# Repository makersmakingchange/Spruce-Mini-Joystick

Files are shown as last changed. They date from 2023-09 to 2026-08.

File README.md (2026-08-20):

 # Spruce Mini Joystick

<!---  SUMMARY A brief summary of the project. What it does, who it is for, how much it costs.  --->
The Spruce Mini Joystick is a mini sized proportional joystick that can be used for adaptive gaming or computer access with a suitable adaptor. Based on a generic PS2-style game controller thumbstick, it has range of motion of ±30° and requires approximately 75 grams-force to fully deflect. This joystick has a two output cables, one with a 3.5 mm TRRS audio plug (i.e., headphone jack) for the joystick, and one with a 3.5 mm mono audio plug for the push switch. 

The Spruce Mini Joystick can be used directly as a left or right thumbstick for the [Microsoft Xbox Adaptive Controller (XAC)](https://www.xbox.com/en-CA/accessories/controllers/xbox-adaptive-controller) using the X1 or X2 analog input ports, or directly with the [PlayStation Access Controller](https://www.playstation.com/en-ca/accessories/access-controller/). It can also be used with the [Forest Joystick Mouse Hub](https://github.com/makersmakingchange/Forest-Joystick-Mouse-Hub) as a USB Gamepad or USB Mouse.

The Spruce Mini Joystick is open assistive technology (OpenAT). Under the terms of the open source licenses, the device may be built, used, and improved upon by anyone.

The current version of the Spruce Mini Joystick (v1.0) has been built and internally tested. It is based on a similar design that has been built and user tested.  

<!---  DEVICE PHOTO  --->
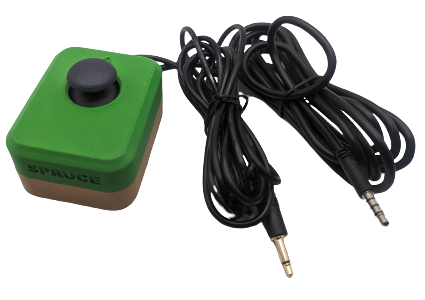
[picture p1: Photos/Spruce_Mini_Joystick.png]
The Spruce Mini Joystick in a brown and green enclosure.
 

**Note:** If experiencing drift when using with the Xbox Adaptive Controller (XAC), unplug and power off the XAC, then power on again and move the joystick in circles.

## Makers Making Change Device Library
  - [Makers Making Change Device Page](https://www.makersmakingchange.com/s/product/spruce-mini-joystick/01tJR000000EHqbYAG)

<!--- 
Other available joysticks can be found through the [Joystick Selection Guide](https://makersmakingchange.com/resource/analog-joystick-selection-guide/)
   --->
   
## OpenAT Joysticks
This design is part of the [OpenAT Joystick project](https://github.com/makersmakingchange/OpenAT-Joysticks), a collection of open source designs for digital access and adapted gaming.  

## How to Obtain a Spruce Mini Joystick
There are several options for obtaining the device.

### 1. Do it Yourself (DIY) or Do it Together (DIT)

This is an open-source assistive technology, so anyone is free to build it. All of the files and instructions required to build the Spruce Mini Joystick are contained within this repository.

### 2. Request a build of this device

If you would like to obtain a Spruce Mini Joystick, you may submit a build request through the [MMC Library Page](https://www.makersmakingchange.com/s/product/spruce-mini-joystick/01tJR000000EHqbYAG). The requestor is responsible for the cost of materials and any shipping.

A limited number of these devices may be available at no-cost to people with disabilities that reside within Canada as part of the [Accesible Technology Program Grant](https://ised-isde.canada.ca/site/accessible-technology-program/en). If you think this applies to you, please send an email to info@makersmakingchange.com.

### 3. How to build this device for someone else
If you have the skills and equipment to build this device, and would like to donate your time to create the joystick for someone who needs it, visit the [MMC Maker Wanted](https://makersmakingchange.com/maker-wanted/) section.

## Getting Started

### 1. Read the Makers Checklist

The Makers Checklist in the [Maker Guide](/Documentation/Spruce_Joystick_Maker_Guide.pdf) contains a list of tasks to complete to build the device.

### 2. Order the Off-The-Shelf Components

The [Spruce Joystick Bill of Materials](/Documentation/Spruce_Joystick_BOM.csv) lists all of the parts and components required to build the Spruce Mini Joystick.

### 3. Print the 3D Printable components

Print the components needed for the Spruce Mini Joystick. Make sure to ask the user if they would like any of the optional prints such as toppers or mount adapters. Refer to the [OpenAT Joystick Setup Guide](https://github.com/makersmakingchange/OpenAT-Joysticks/Resources/OpenAT_Joystick_Setup_Guide.pdf) for detailed mounting options. 

The 3D print files for the mounting adapters are located on the [OpenAT Joystick Repository](https://github.com/makersmakingchange/OpenAT-Joysticks/tree/main/Mounting%20Adapters)

All of the files and individual print files can be in the [/Build_Files/3D_Printing_Files](/Build_Files/3D_Printing_Files/) folder.

### 4. Assemble the Spruce Mini Joystick

Reference the [Maker Guide](/Documentation/Spruce_Joystick_Maker_Guide.pdf) for the tools and steps required to build each portion.

## Files
### Documentation
| Document             | Version | Link |
|----------------------|---------|------|
| Design Rationale     | 1.0     | [Spruce_Mini_Joystick_Design_Rationale](/Documentation/Spruce_Joystick_Design_Rationale.pdf)     |
| Bill of Materials    | 1.0     | [Spruce_Mini_Joystick_Bill_of_Materials](/Documentation/Spruce_Joystick_BOM.csv)     |
| Maker Guide          | 1.0     | [Spruce_Mini_Joystick_Maker_Guide](/Documentation/Spruce_Joystick_Maker_Guide.pdf)     |
| User Guide           | 1.0.1     | [Spruce_Mini_Joystick_User_Guide](/Documentation/Spruce_Joystick_User_Guide.pdf)    |

### Design Files
<!--- DESIGN FILES If possible, include a copy of original design files to facilitate easy editing and customization. --->
 - [CAD Files](/Design_Files)

### Build Files
<!--- BUILD FILES This section lists links to the various files used to build the device. --->
 - [3D Printing Files](/Build_Files/3D_Print_files)

## License
Copyright (c) 2023 Neil Squire / Makers Making Change.

This repository describes Open Hardware:
 - Everything needed or used to design, make, test, or prepare the Spruce Mini Joystick is licensed under the [CERN 2.0 Weakly Reciprocal license (CERN-OHL-W v2) or later](https://cern.ch/cern-ohl ) .
 - Accompanying material such as instruction manuals, videos, and other copyrightable works that are useful but not necessary to design, make, test, or prepare the Spruce Mini Joystick are published under a [Creative Commons Attribution-ShareAlike 4.0 license (CC BY-SA 4.0)](https://creativecommons.org/licenses/by-sa/4.0/) .

You may redistribute and modify this documentation and make products using it under the terms of the [CERN-OHL-W v2](https://cern.ch/cern-ohl).
This documentation is distributed WITHOUT ANY EXPRESS OR IMPLIED WARRANTY, INCLUDING OF MERCHANTABILITY, SATISFACTORY QUALITY AND FITNESS FOR A PARTICULAR PURPOSE.
Please see the CERN-OHL-W v2 for applicable conditions.

Source Location: https://github.com/makersmakingchange/Spruce-Mini-Joystick

## Attribution
<!--- ATTRIBUTION Include any information related to the development of the design. This may include who identified the initial challenge, who contributed to the design --->
Hardware and enclosure design: Josie Versloot, Neil Squire Society

Enclosure design based on [snap assembly thumbstick shell](https://www.printables.com/model/508909-snap-assembly-thumbstick-shell/files) by [AbleGamers Charity](https://ablegamers.org/).

A range of toppers are availablef or this joystick and utilize the mofels found in the [set of toppers created by AbleGamers Charity](https://www.printables.com/model/501869-analog-thumbstick-topper-collection).

The documentation template was created by Makers Making Change / Neil Squire and is used under a CC BY-SA 4.0 license. It is available at the following link: https://github.com/makersmakingchange/OpenAT-Template

---

<!-- ABOUT MMC START -->
## About Makers Making Change
[Makers Making Change Logo](https://www.makersmakingchange.com/)

Makers Making Change is a program of [Neil Squire](https://www.neilsquire.ca/), a Canadian non-profit that uses technology, knowledge, and passion to empower people with disabilities.

Makers Making Change leverages the capacity of community based Makers, Disability Professionals and Volunteers to develop and deliver affordable Open Source Assistive Technologies.

 - Website: [www.MakersMakingChange.com](https://www.makersmakingchange.com/)
 - GitHub: [makersmakingchange](https://github.com/makersmakingchange)
 - Bluesky: [@makersmakingchange.bsky.social](https://bsky.app/profile/makersmakingchange.bsky.social)
 - Instagram: [@makersmakingchange](https://www.instagram.com/makersmakingchange)
 - Facebook: [makersmakechange](https://www.facebook.com/makersmakechange)
 - LinkedIn: [Neil Squire Society](https://www.linkedin.com/company/neil-squire-society/)
 - Thingiverse: [makersmakingchange](https://www.thingiverse.com/makersmakingchange/about)
 - Printables: [MakersMakingChange](https://www.printables.com/@MakersMakingChange)

### Contact Us
For technical questions, to get involved, or to share your experience we encourage you to [visit our website](https://www.makersmakingchange.com/) or [contact us](https://www.makersmakingchange.com/s/contact).
<!-- ABOUT MMC END -->

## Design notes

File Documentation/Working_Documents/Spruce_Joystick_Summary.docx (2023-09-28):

This document is intended to be a summary of a device to make it easier to add to the website.

# Product Information

## Product Name

Spruce Mini Joystick

## Device Category

Adapted Toys

Aids for Daily Living (ADL)

Assistive Switches

Communication Aids (AAC)

Computer Access

Environmental Controls

Gaming

Keyguard

Kits

LipSyncs

Mounting

Recreation and Leisure

Seating and Positioning

Switch Interfaces

Writing Aids

## User Value Statement

If you're looking for a standard joystick with a small range of motion and push button feature, we'd like to point you to the Spruce Mini Joystick.

## Designer

Josie Versloot

# Device Info

## Overview

The Spruce Mini Joystick is a small joystick compatible with the Forest Joystick Mouse Hub (https://github.com/makersmakingchange/Forest-Joystick-Mouse-Hub), Xbox Adaptive Controller, or other analog input joystick devices. It currently has a range of toppers available created by AbleGamers Charity (https://www.printables.com/model/501869-analog-thumbstick-topper-collection).

## Disability Type

Select one or more disability types:

Agility / Dexterity

Arthritis

Cognitive

Hearing

Mobility

Mobility

Other

Pain

SCI

Vision

## Disability Type Description

## This device is designed for users with a small range of motion that need an external joystick for adaptive gaming or computer access.

## How To Use

For full instructions please refer to the User Guide.

Usage

Using the Joystick

1. Plug the 3.5 mm TRRS cable from the joystick into the host device (such as the Xbox Adaptive Controller). If using the Xbox Adaptive Controller, plug it into X1 to use at the left joystick, or plug into X2 to use as the right joystick.

2. Ensure the arrow on the joystick is pointing in the “up/forward” direction, away from the user.

3. Mount the device if needed (see below).

4. Move joystick as you would with a standard controller. Estimated Cost

Compatibility

This device is compatible with the Xbox Adaptive Controller, Forest Joystick Mouse Hub (https://github.com/makersmakingchange/Forest-Joystick-Mouse-Hub), Enabled Controller Mini (https://github.com/makersmakingchange/Enabled-Controller-Mini/tree/main), and any other device that accepts a TRRS analog joystick input.

## Estimated Cost

The estimated material cost of the device:

$0 - $10

$11 - $25

$26 - $50

$51 - $100

$101 - $250

$250+

## Attribution

Hardware and enclosure design: Josie Versloot, Neil Squire Society

Enclosure design remixed from AbleGamers Charity (https://www.printables.com/model/508909-snap-assembly-thumbstick-shell/files), originally released under a Creative Commons (4.0 International License) Attribution-NonCommercial

(http://creativecommons.org/licenses/by-nc/4.0/)

The documentation template was created by Makers Making Change / Neil Squire and is used under a CC BY-SA 4.0 license. It is available at the following link: https://github.com/makersmakingchange/OpenAT-Template

# Maker Info

## Project Skills

3D Printing

Custom PCB

Electronics

Laser Cutting

Mechanics

Other

Software

Soldering

Woodworking

## Skills Description

This is an intermediate build requiring electronics, mechanics, and 3D printing.

## Tools Needed

3D Printer

Common Hand Tools

Common Power Tools

Laser Cutter

Soldering Iron

Specialized Tooling

## Print time (hrs)

<Estimated total print time in numerical hours>

## Assembly time (hrs)

<Estimated assembly time in numerical hours>

## Build Instructions

For full instructions please refer to the Maker Guide.

Print Settings:

- 0.2mm Layer Height
- 20% infill

## Download Link

https://github.com/makersmakingchange/Spruce-Mini-Joystick/archive/refs/heads/main.zip

## Project Link

https://github.com/makersmakingchange/Spruce-Mini-Joystick

# License

## License

Hardware: CERN OHL 2.0 w

Documentation: Attribution-ShareAlike 4.0 International

© 2023 by Neil Squire Society. This work is licensed under the CC BY SA 4.0 License: http://creativecommons.org/licenses/by-sa/4.0 Files available at https://github.com/makersmakingchange/Spruce-Mini-Joystick Page 1 of 2

V1.0 | September 2023 Spruce Mini Joystick Summary

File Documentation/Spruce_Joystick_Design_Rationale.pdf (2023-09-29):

V1.0 | SEPTEMBER 2023

## Spruce Mini Joystick

## DESIGN RATIONALE

© 2023 by Neil Squire Society. (https://www.neilsquire.ca/) This work is licensed under the CC BY SA 4.0 License: http://creativecommons.org/licenses/by-sa/4.0 Files available at https://github.com/makersmakingchange/Spruce-Mini-Joystick

### Introduction

There is an identified need for cost-effective analog joysticks that can be used with the Xbox Adaptive Controller (XAC). There are currently not very many commercial joysticks on the market, and the ones that are can be costly. This joystick is intended to be used with the XAC for anyone who may find it easier to game with a joystick.

There is also a need for alternative mouse options that are affordable, and some people may find a joystick easier to use than a standard mouse. This mouse needs to be a standalone device or combination of devices that can be used with PC and can complete the basic mouse functions such as left click.

This joystick specifically is meant for someone with a lower range of motion and lower force compared to some USB joysticks.

### Research

### Commercial Joysticks

Name | Price | Link | Picture
Ultra-Stik | 95 UK | Accessible Gaming Shop -Ultra-Stik -OneSwitch.org.uk (https://www.oneswitch.org.uk/art.php?id=17)

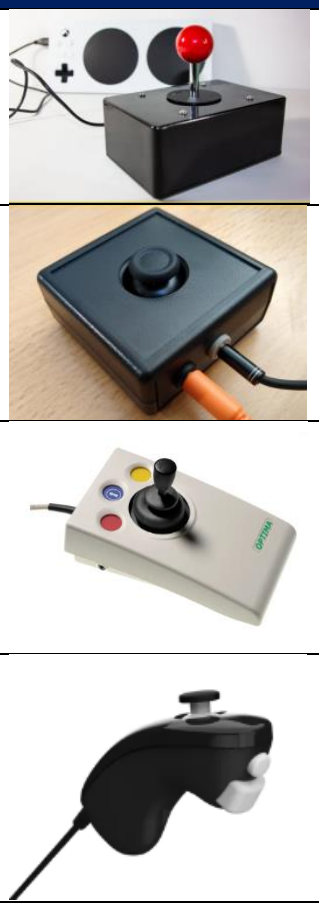
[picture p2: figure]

XAC MINI Stick | 105 UK | XAC Mini Joystick -OneSwitch.org.uk (https://www.oneswitch.org.uk/art.php?id=270)
Optima Joystick | 219.60 UK | Optima Joystick - Video Gaming Assistive Joystick (pretorianuk.com) (https://www.pretorianuk.com/optima-joystick)
PDP One-Handed Joystick for Xbox Adaptive Controller | Discontinued | PDP One-Handed Joystick for Xbox Adaptive Controller (microsoft.com) (https://www.microsoft.com/en-ca/d/pdp-one-handed-joystick-for-the-xbox-adaptive-controller/8qhw8mlwpp1l)

## DESIGN RATIONALE

© 2023 by Neil Squire Society. (https://www.neilsquire.ca/)

XAC Flat Thumbstick | $74.95 | XAC Flat Thumbstick (evilcontrollers.com) (https://www.evilcontrollers.com/xac-flat-thumbstick)

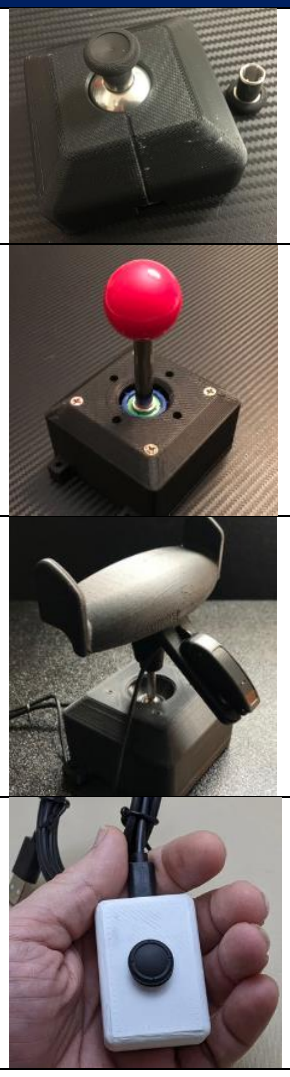
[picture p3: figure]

Name | Price | Link | Picture
MINISTIX-TU | $75 | MINISTIX-TU (USB Version) — Warfighter Engaged (https://warfighterengaged.org/shop/ministix-tu)
DPAD-T | $65 | DPAD-T — Warfighter Engaged (https://warfighterengaged.org/shop/dpad-t)
JOYSTIX-FPS | $75 | JOYSTIX-FPS — Warfighter Engaged (https://warfighterengaged.org/shop/joystix-l-aenef)
JoyCon® Style Joystick For XBOX® Adaptive Controller & PC (JoyToKey) | $60.40 | Joycon® Style Joystick for XBOX® Adaptive Controller & PC | Etsy Canada (https://www.etsy.com/ca/listing/1205880837/joycon-style-joystick-for-xbox-adaptive?click_sum=ba40a784&crt=1)

### Ideation

### Joystick Element

For this design, the same joystick element will be used as the current Analog Thumbstick on the website, which is a standard PS2 thumbstick unit.

There is also an Adafruit version of a similar joystick, this will be investigated as well and the price and availability will be compared.

### Switch Input

There are a few different ways that switch input can be accomplished:

## DESIGN RATIONALE

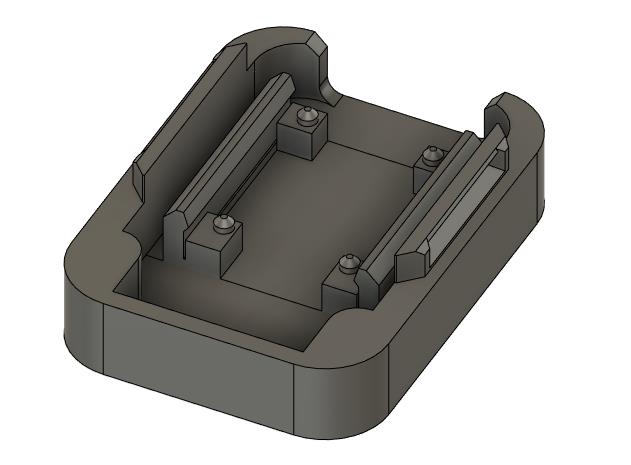
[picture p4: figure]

© 2023 by Neil Squire Society. (https://www.neilsquire.ca/)

- Integrated buttons
- Integrated switch jacks
- Separate “controller box” that the joystick and switches plug into

The first iteration of this design is now the Cedar Mini Joystick which had integrated jacks, where the users could plug in their assistive switch of choice for switch input. While in mouse mode, these switches are left click, right click, and scroll.

After user testing, the decision was made to proceed with the separate “controller box” or “hub” that the joystick and switches plug into.

### Conceptual Design

The enclosure design for this joystick was based on the AbleGamers “snap assembly thumbstick shell” in Printables. (https://www.printables.com/model/508909-snap-assembly-thumbstick-shell)

### Concept 1: Joystick snap in assembly

For this, the joystick would snap into the enclosure like it does in the original AbleGamers design.

## DESIGN RATIONALE

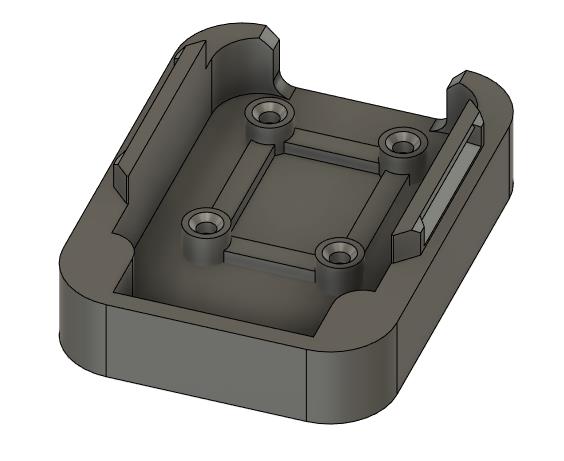
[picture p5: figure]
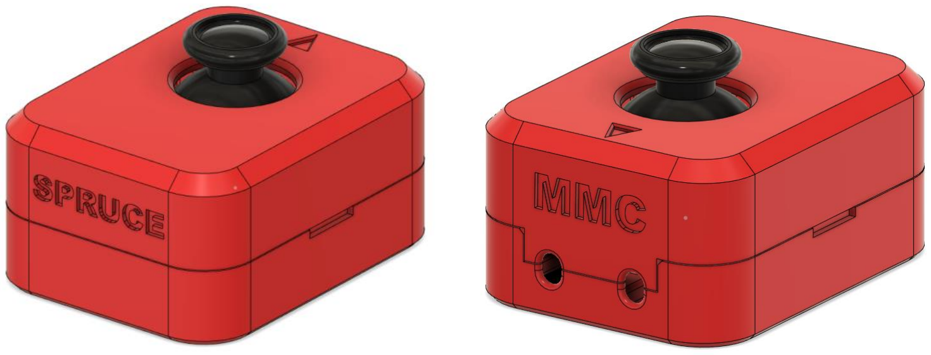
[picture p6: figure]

© 2023 by Neil Squire Society. (https://www.neilsquire.ca/)

### Concept 2: Joystick screw in assembly

### Detailed Design

### Overview

On the outside of the enclosure, there are a few key features. On the side facing the user, “Spruce” is engraved, and on the side facing away from the user “MMC” is engraved. There is also an arrow on the top of the enclosure showing the up direction.

There are two cables that exit the back side of the enclosure (away from the user), both are 3.5 mm audio cables. One of the cables has 4 conductors (TRRS cable) for the joystick output, and one has 2 conductors (mono cable) for the switch output for the press down switch built into the joystick. It was

## DESIGN RATIONALE

© 2023 by Neil Squire Society. (https://www.neilsquire.ca/) decided that these cables would exit away from the user for better cable management and to be the most out of the way while the joystick is in use.

Joystick Unit
For this joystick, there are two main joystick/thumbstick units that can be used. Some are commercially available for hobbyists from a few different sources such as Amazon, and then the other unit is the “Adafruit 2-axis Thumb Joystick with Select Button + Breakout Board” which available from some electronics suppliers such as DigiKey and Mouser.

Comparing these two joystick units, the ones from Amazon are significantly less expensive, at $20.89 for a pack of 10, whereas the Adafruit unit is $9.13 on DigiKey for one unit. For a single build the Adafruit unit would be less expensive, but for 2 or more units it would make sense to use the units from Amazon.

Another consideration here is availability. The Adafruit unit goes in and out of stock, but when it comes back in stock it is the same unit. There seem to be more Amazon units in stock, but they could go out of stock at any time. If they go out of stock a comparable unit can often be found, but it might not be exactly the same, which leads to the point of consistency across units.

Lastly, the consistency and quality of the joystick unit should be considered. The Adafruit unit is going to be more consistent and is guaranteed to always be the same dimensions and quality. Whereas if the Amazon unit goes out of stock and another unit has to be sourced it is not guaranteed to be exactly the same, and the hole spacing and overall quality could be different.

For this iteration of the design, two sets of holes were included so either joystick unit could be used.

### Wiring

Wiring diagram
To wire the joystick the Xbox Adaptive Controller analog input convention will be used with a 3.5 mm TRRS audio cable. Since the joystick has a built-in button as well, an additional 3.5 mm mono audio cable will be used as well.

Table 1. XAC Analog Joystick Input Convention

JOYSTICK | TRRS PLUG
X-AXIS | Tip
Y-AXIS | Ring 1
GND | Ring 2
VCC | Sleeve

## DESIGN RATIONALE

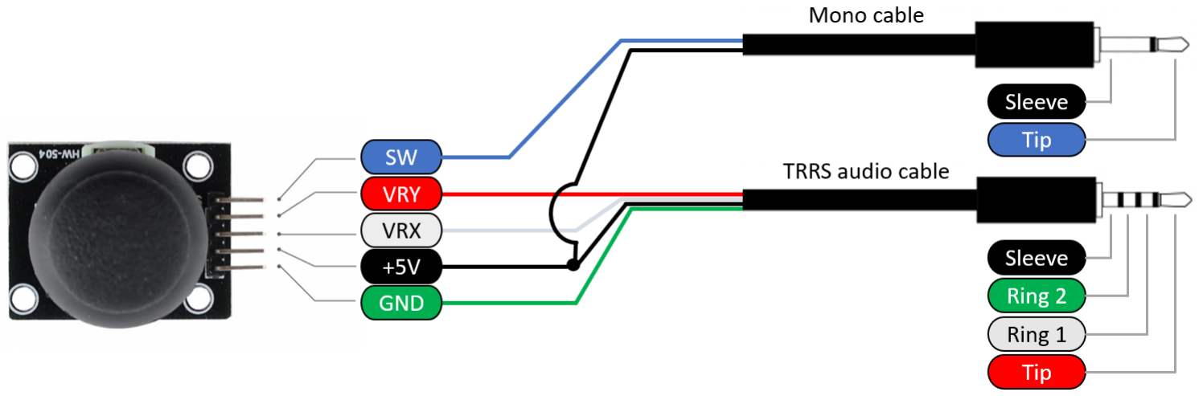
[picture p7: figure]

© 2023 by Neil Squire Society. (https://www.neilsquire.ca/)

Generic PS2 Joystick Wiring

Figure 1. Generic PS2 Wiring Diagram

Table 2. Generic PS2 Wiring Guide

JOYSTICK BOARD LABEL | DIGIKEY TRRS CABLE | TRRS PLUG | MONO CABLE | MONO PLUG
SW | --- | --- | Red | Tip
VRY | Red | Tip | | ---
VRX | White | Ring 1 | | ---
+5V | Black | Sleeve | | ---
GND | Green | Ring 2 | White | Sleeve
Table 1 lists the wiring connections and colors for the DigiKey TRRS and mono cables.

## DESIGN RATIONALE

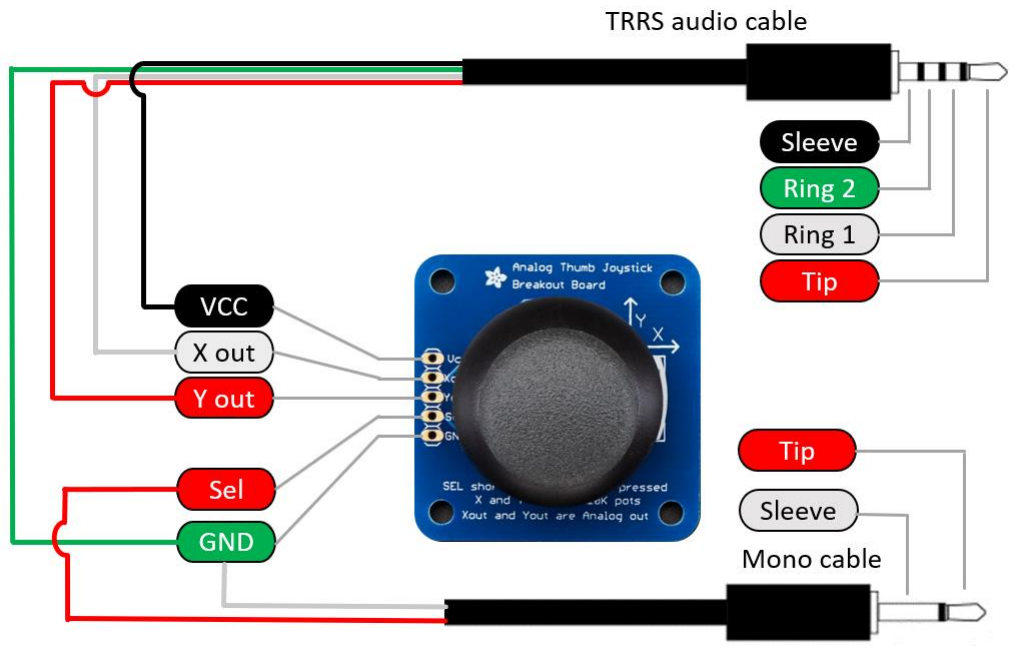
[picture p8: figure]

© 2023 by Neil Squire Society. (https://www.neilsquire.ca/)

Adafruit Joystick Wiring

Adafruit Joystick Wiring diagram

Figure 2. Adafruit Joystick Wiring Diagram

Table 3. Adafruit Joystick Wiring

JOYSTICK BOARD Label | TRRS Plug | DigiKey TRRS Cable | Your TRRS CABLE | Mono PLUG | Mono CABLE | Your Mono Cable
Sel | --- | --- | | Tip | Red
Yout | Tip | Red | | --- | ---
Xout | Ring 1 | White | | --- | ---
Vcc | Sleeve | Black | | --- | ---
GND | Ring 2 | Green | | Sleeve | White

## DESIGN RATIONALE

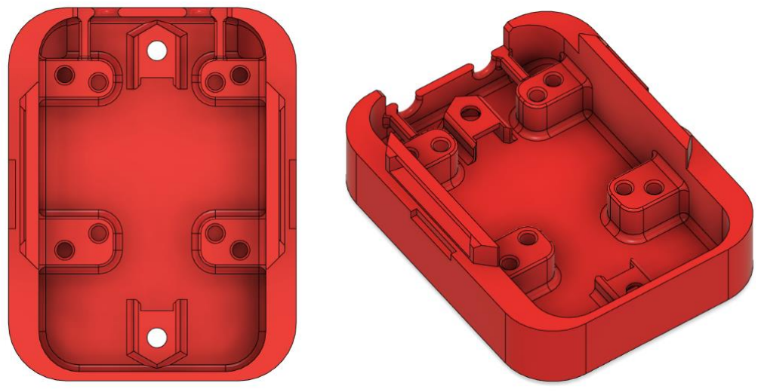
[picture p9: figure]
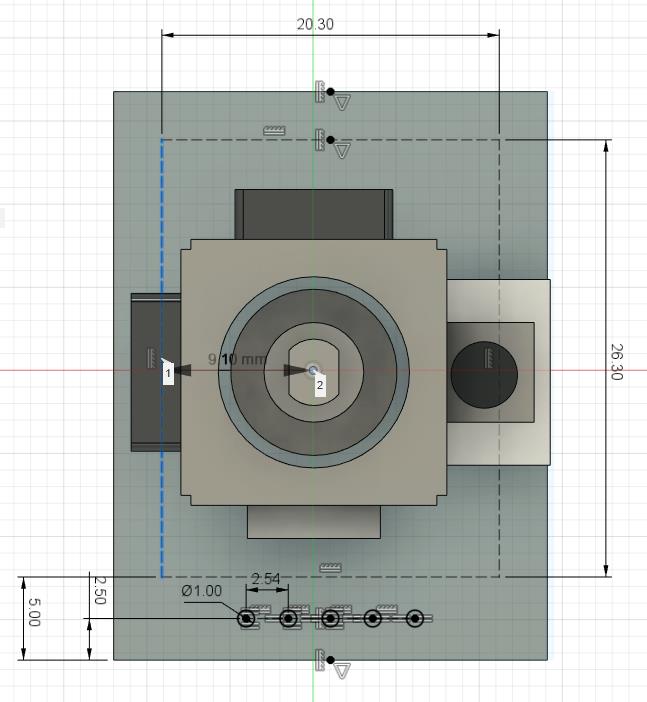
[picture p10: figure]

© 2023 by Neil Squire Society. (https://www.neilsquire.ca/)

### Enclosure Bottom

Joystick Mounting
For the two sets of mounting holes, it was decided to use a #4 sheet metal self tapping screw like other MMC designs such as the Oak Compact Joystick and the MMC60 switch. The thread diameter of this screw is 2.8 mm, and the best practice for the hole size for self tapping screws (https://www.hydraresearch3d.com/design-rules#threads-post-process) is 96% of the hole diameter, so a hole size of 2.68 mm was used.

The spacing of the holes for the Amazon unit is seen below:

The Adafruit joystick unit has the holes in a square with the joystick centered between the screw holes. The spacing of these screw holes is 30.48 mm as seen below:

## DESIGN RATIONALE

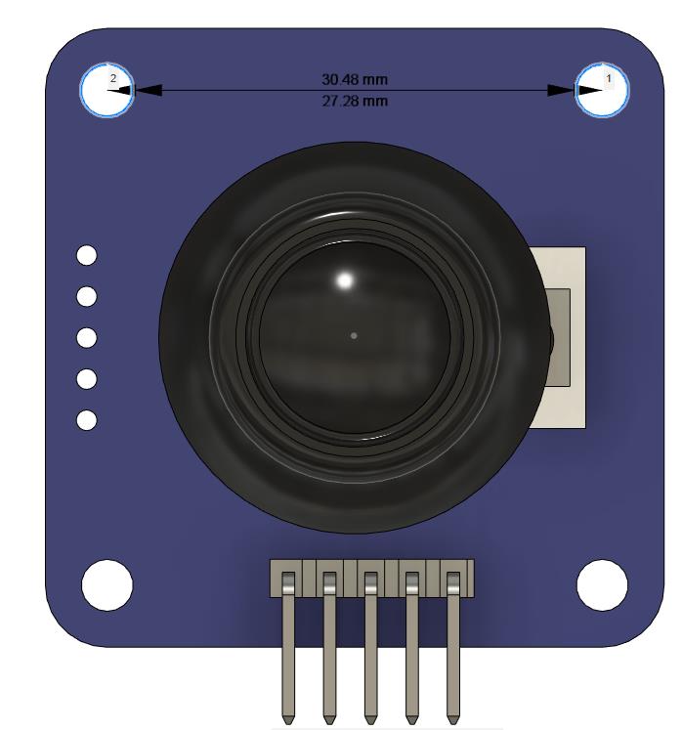
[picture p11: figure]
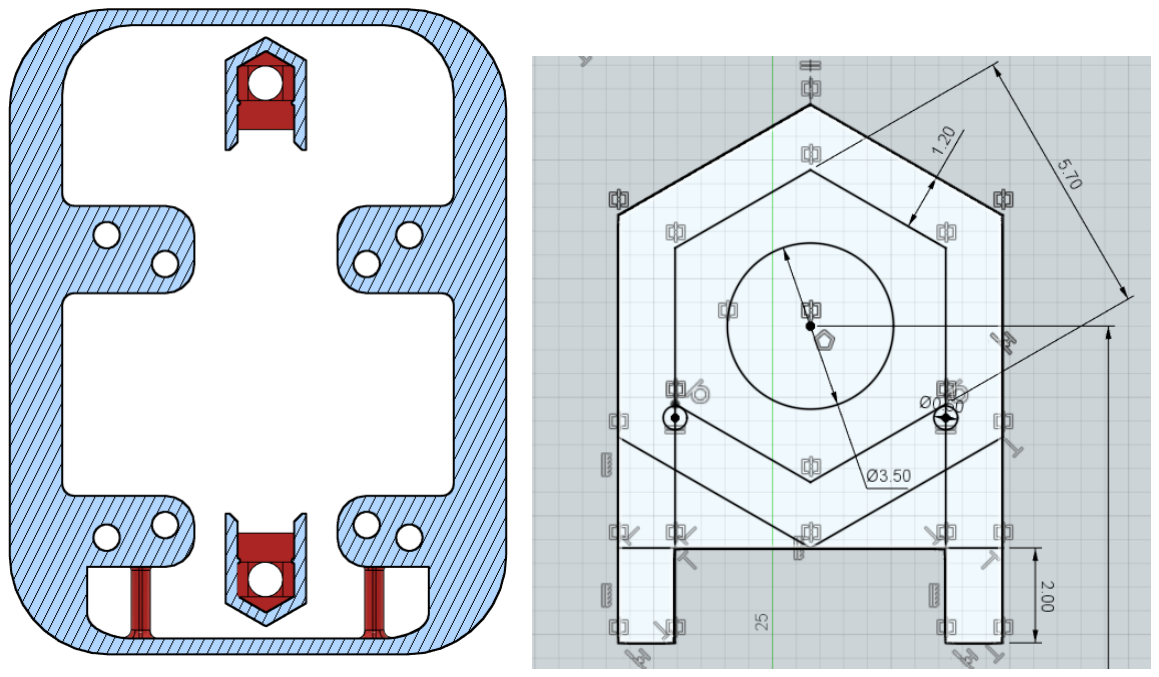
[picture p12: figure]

© 2023 by Neil Squire Society. (https://www.neilsquire.ca/)

Mounting – Captive Nuts
It was decided that this design should incorporate a way to mount the joystick when not used on a tabletop. To do this, two slots for captive nuts were added, which would then screw into a separate mount adapter which will have the mounting hardware in it. Here, two M3 hex nuts are used. The centres of these nuts are 50.0 mm apart. There are also small walls added coming out of these captive nut slots to help with alignment of the nut while inserting. These two slots are seen in the photos above, and then in a closer view below. As seen in the photo, around the hole above the captive nut, which would be printed unsupported, there are small single layer rectangles, this is a best practice when 3D printing unsupported holes. (https://www.hydraresearch3d.com/design-rules#unsupported-holes)

## DESIGN RATIONALE

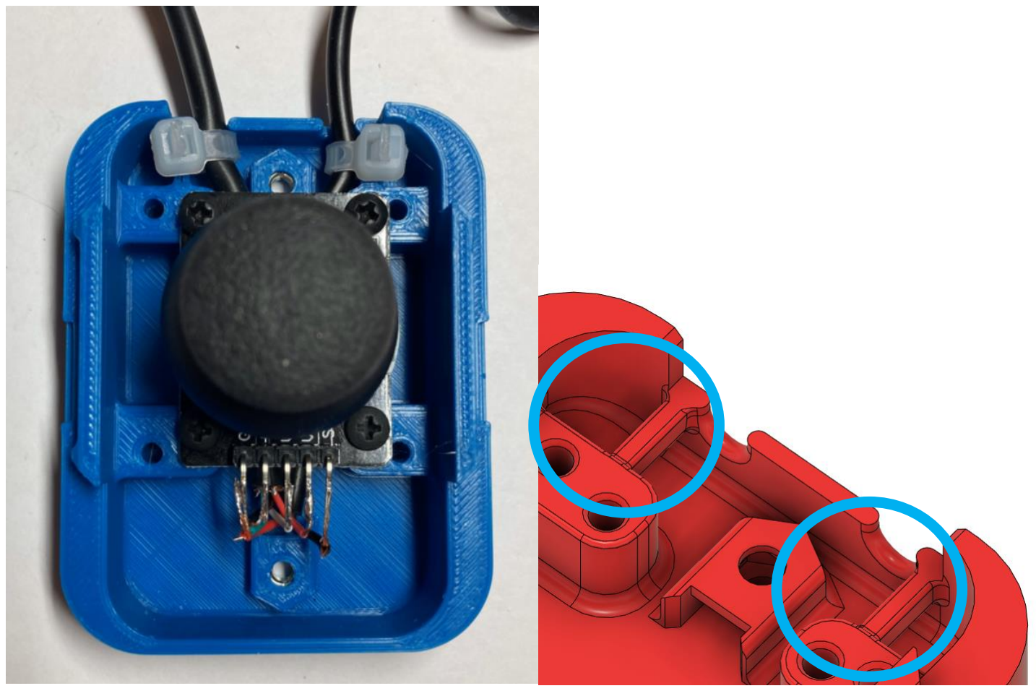
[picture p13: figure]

© 2023 by Neil Squire Society. (https://www.neilsquire.ca/)

Cable Strain Relief

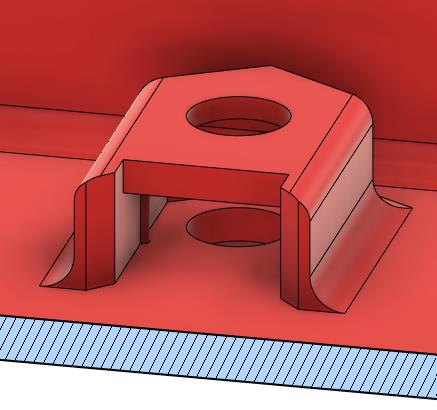
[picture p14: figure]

Strain relief for the two cables exiting the enclosure was added by adding two small beams where a zip tie could be fastened for each of the cables before they exit the enclosure. The zip ties are shown with the cables in the photo below, and the beams are circled in a picture from the CAD.

Enclosure Snap Fit
This design uses a snap fit to connect the top of the enclosure to the bottom of the enclosure.

The piece on the bottom of the enclosure was extruded inwards (cut away from body) 3mm at a taper angle of 45 degrees. The top lip was then chamfered so the top could be inserted easier. The same sketch was used for the top of the enclosure to extrude out 3 mm at a taper angle of 45 degrees, and then the tip was chamfered. The distance between the two surfaces before adding the snap fit was 0.3mm.

## DESIGN RATIONALE

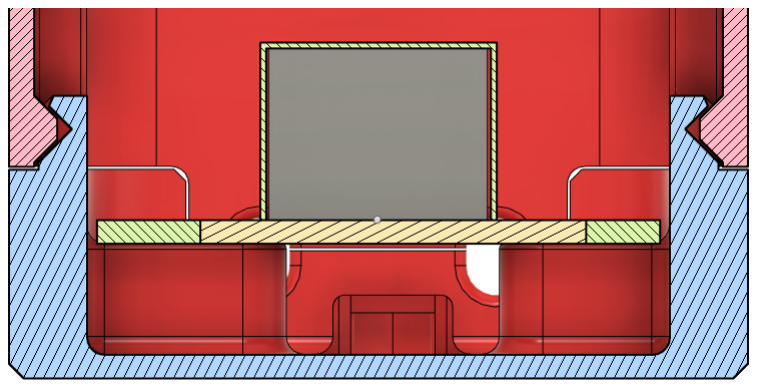
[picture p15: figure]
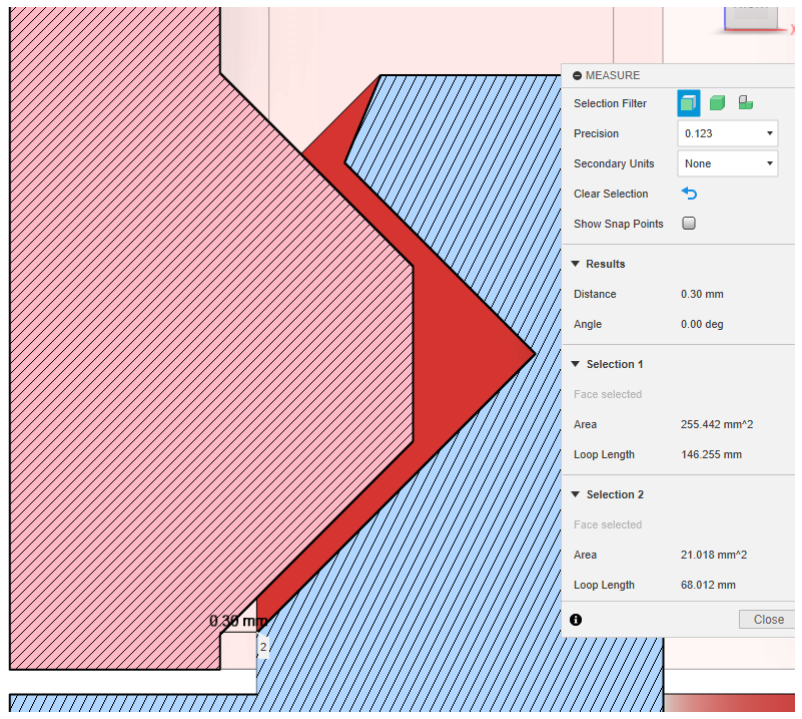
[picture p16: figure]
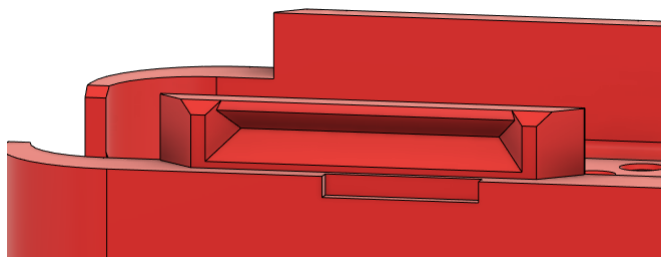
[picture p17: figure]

© 2023 by Neil Squire Society. (https://www.neilsquire.ca/)

Piece on the bottom enclosure:

Piece on the top enclosure:

## DESIGN RATIONALE

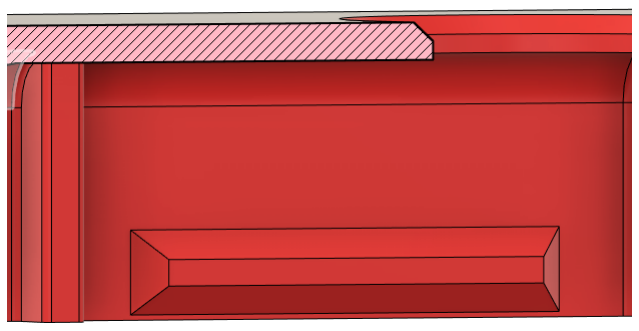
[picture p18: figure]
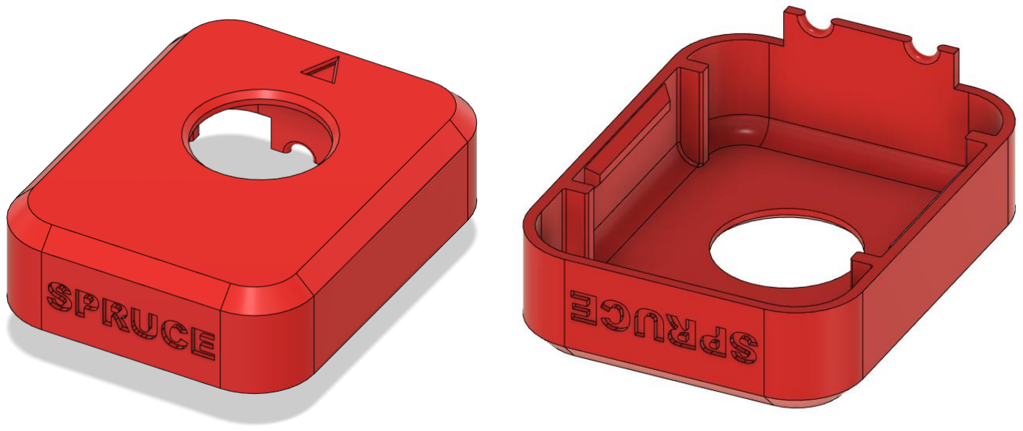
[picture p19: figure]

© 2023 by Neil Squire Society. (https://www.neilsquire.ca/)

### Enclosure Top

During User Testing with the Cedar Mini Joystick (which used the same joystick unit) it was identified that it is important to not have a large gap between the joystick unit and the enclsoure, where the electronisc can be seen and things could fall into the enclosure during use, such as crumbs or other debris. For this reason, the height on this enclosure was increased and the size of the hole around the joystick was decreased, to decrease this gap.

## DESIGN RATIONALE

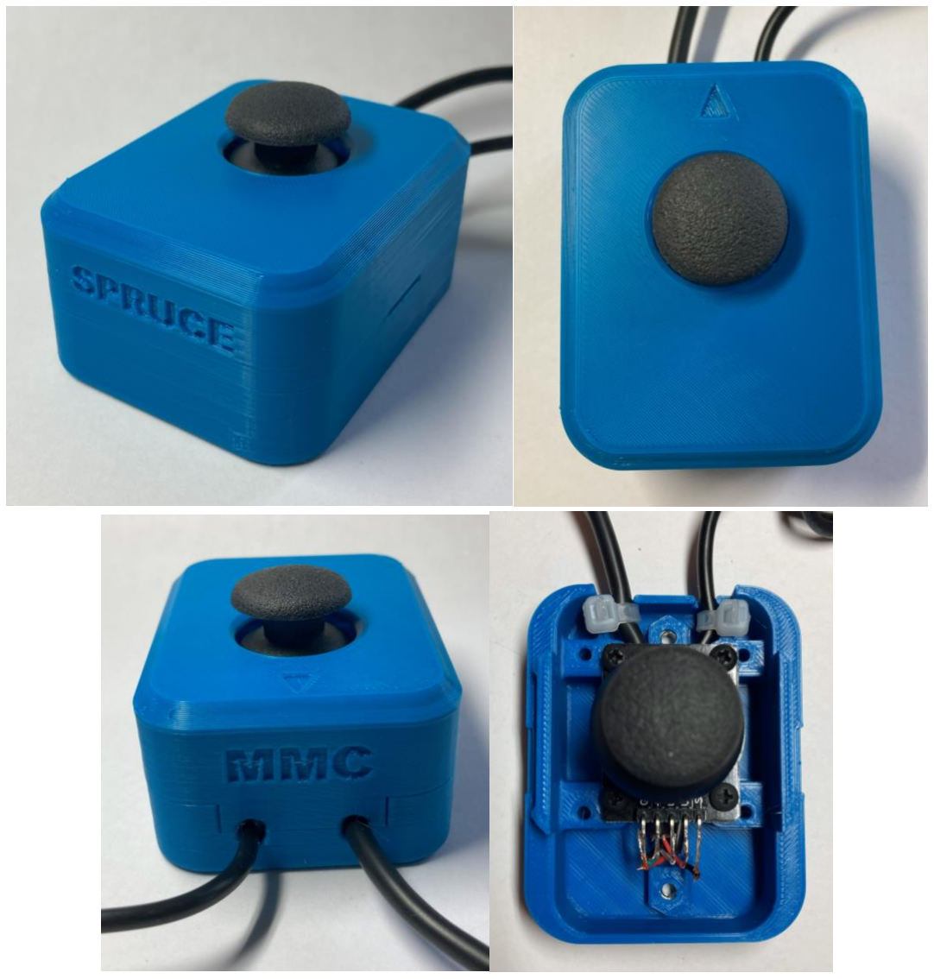
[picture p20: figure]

© 2023 by Neil Squire Society. (https://www.neilsquire.ca/)

### Assembled Prototype

### Opportunities for Improvement

- Could reduce the height of the enclosure, if possible to keep the fit around the joystick topper
- Add a feature to the outside of the enclosure to allow for snap on pieces for wrist supports and other bases

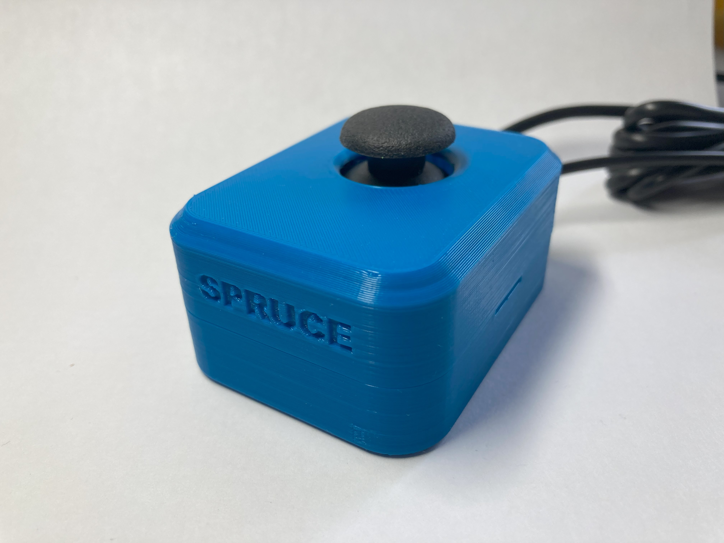
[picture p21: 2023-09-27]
Photos/Spruce_Mini_Joystick_front.jpg

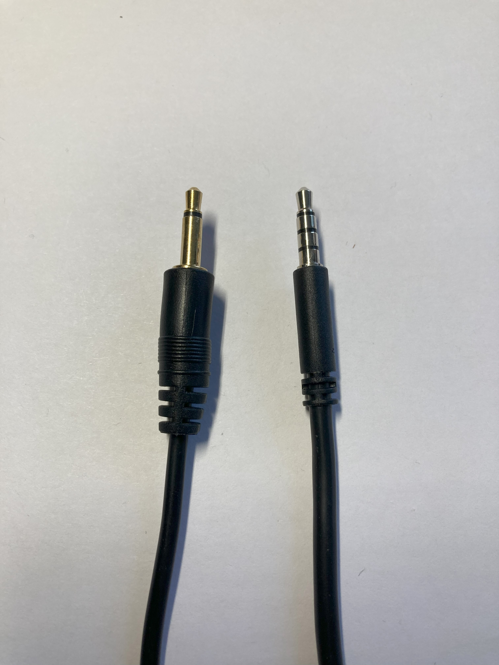
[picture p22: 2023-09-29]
Photos/Mono_and_TRRS_cables.jpg

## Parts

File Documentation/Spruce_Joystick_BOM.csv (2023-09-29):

Spruce Mini Joystick |  |  |  |  |  |  |  | Unit Cost | Total Cost | Total Print time (hr) | Total filament (g)
Version: V1.0 |  | Last Updated: 2023-Sept-25 |  |  |  |  |  | $33.18 | $33.18 | 3.13 | 28
Commercial Parts
 | Part Name | Source | QTY | QTY/PKG | $/PKG | PKG QTY | $/Unit | Extended | Total | Link
 | Joystick unit - Adafruit | DigiKey | 1 | 1 | 9.13 | 1 | $9.13 | $9.13 | $9.13 | https://www.digikey.ca/en/products/detail/adafruit-industries-llc/512/7056915
 | TRRS 3.5 mm Audio Cable | DigiKey | 1 | 1 | $7.29 | 1 | $7.29 | $7.29 | $7.29 | https://www.digikey.ca/en/products/detail/tensility-international-corp/10-00341/2350244
 | Mono 3.5 mm Audio cable | DigiKey | 1 | 1 | $4.62 | 1 | $4.62 | $4.62 | $4.62 | https://www.digikey.ca/en/products/detail/tensility-international-corp/10-00344/2350247
 | 4" cable tie | DigiKey | 2 | 1 | $0.25 | 2 | $0.25 | $0.50 | $0.50 | https://www.digikey.ca/en/products/detail/te-connectivity/2-604771-9/2259327
 | #4 Metal Screw, 3/8″ Length (if building more than two, link below) | DigiKey | 4 | 1 | $0.60 | 4 | $0.60 | $2.40 | $2.40 | https://www.digikey.ca/en/products/detail/serpac/6005/307599
 | M3 hex nut | DigiKey | 2 | 1 | $0.27 | 2 | $0.27 | $0.54 | $0.54 | https://www.digikey.ca/en/products/detail/keystone-electronics/4708/4499301
 | Digikey shipping (if spending less than $100) | DigiKey | 1 | 1 | $8.00 | 1 | $8.00 | $8.00 | $8.00
3D Printed Parts ESTIMATED PRICING USING 1KG ROLL COST: |  | $25.00
 | Part | Material | QTY | Mass (g) / Unit | Time / Unit |  | Print Time (Min) | Estimated Price |  | Link
 | Spruce Enclosure Bottom | PLA | 1 | 16 | 106 |  | 106 | $0.40
 | Spruce Enclosure Top | PLA | 1 | 12.0 | 82 |  | 82 | $0.30
Alternatives
ID | Part and description | Source | QTY | QTY/PKG | $/PKG | PKG QTY | $/Unit | Extended | Total | Link
 | #4 Metal Screw, 3/8″ Length, 100 pack | Amazon | 8 | 100 | $9.30 | 1 | $0.09 | $0.74 | $9.30 | https://a.co/d/523bJeL
 | Cable tie | DigiKey | 1 | 1 | $0.15 | 1 | $0.15 | $0.15 | $0.15 | https://www.digikey.ca/en/products/detail/heyco-products-corporation/13123B/15791902
 | Cable tie | Your local dollarstore
 | Joystick (PS2) | Amazon | 1 | 10 | $20.89 | 1 | $2.09 | $2.09 | $20.89 | https://www.amazon.ca/dp/B089VXPHDH?_encoding=UTF8&psc=1&ref_=cm_sw_r_cp_ud_dp_GGTEDME4PM2P27SG86P7
 | Joystick unit - Adafruit | Mouser | 1 | 1 | 8.63 | 1 | $8.63 | $8.63 |  | https://www.mouser.ca/ProductDetail/Adafruit/512?qs=GURawfaeGuBuwf9HaRK7%252BA%3D%3D
 | (Optional for mount) M3x12mm screw x2 | Mechanical | 0 | 1 | $1.11 | 0 | $1.11 | $- | $- | https://www.digikey.ca/en/products/detail/apm-hexseal/RM3X12MM-2701/2063201
 | (Optional for mount) Tee nut (source from local hardware store) | Mechanical | 0 | 1 | $0.48 | 0 | $0.48 | $- | $- | https://www.homedepot.ca/product/paulin-1-4-inch-20-tee-nuts-4-prong-5-16-inch-barrel-length/1000129429

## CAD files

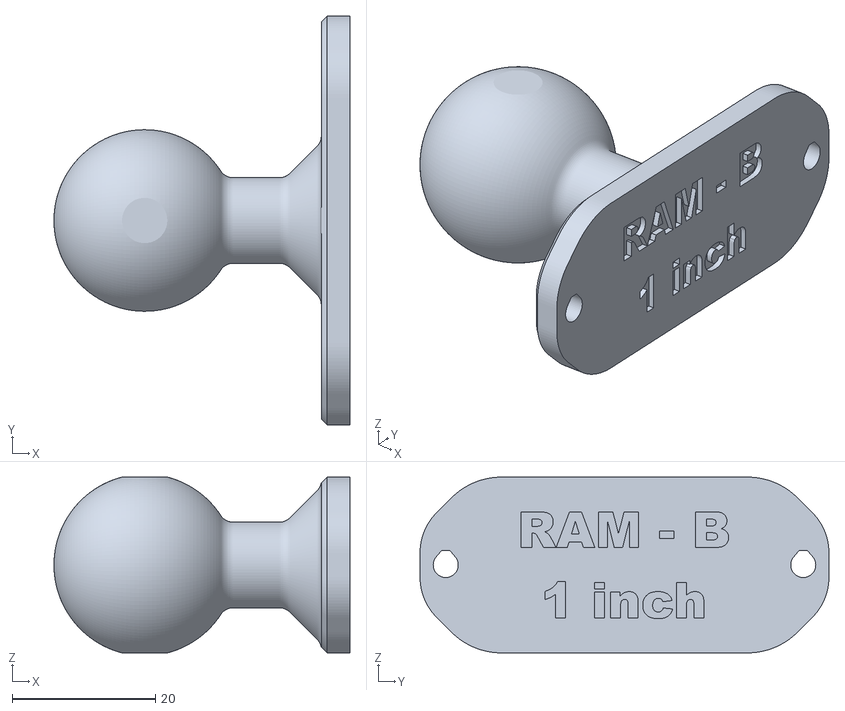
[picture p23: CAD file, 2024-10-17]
Build_Files/3D_Printing_Files/Joystick_RAM_B_Mount_Adapter.stl
41.4 x 57.2 x 24.6

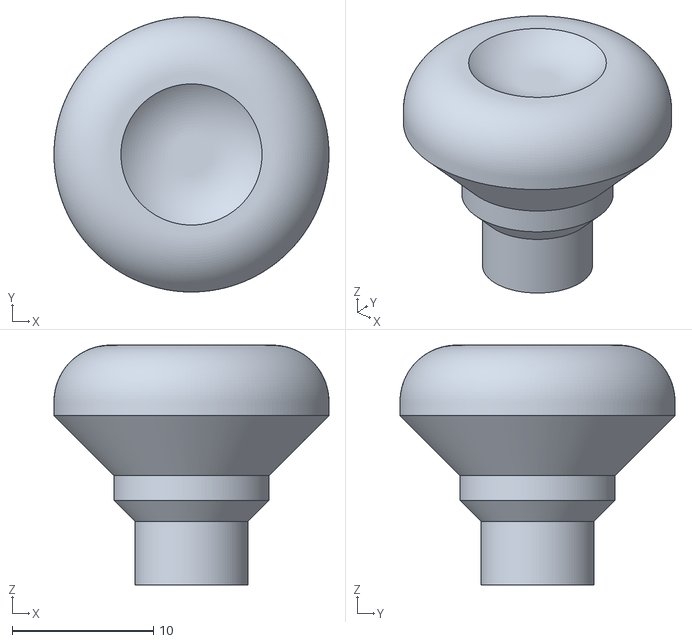
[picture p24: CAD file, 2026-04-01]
Build_Files/3D_Printing_Files/Toppers/Additional_Toppers/standard.stl
19.5 x 19.5 x 17.0

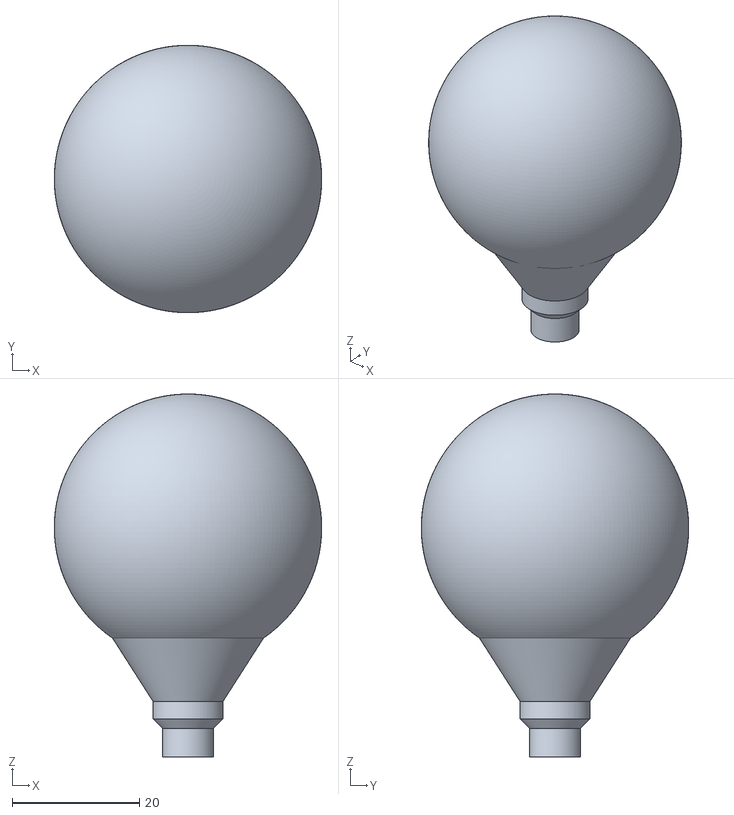
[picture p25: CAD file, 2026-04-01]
Build_Files/3D_Printing_Files/Toppers/Ball_Topper.stl
42.0 x 42.0 x 57.0

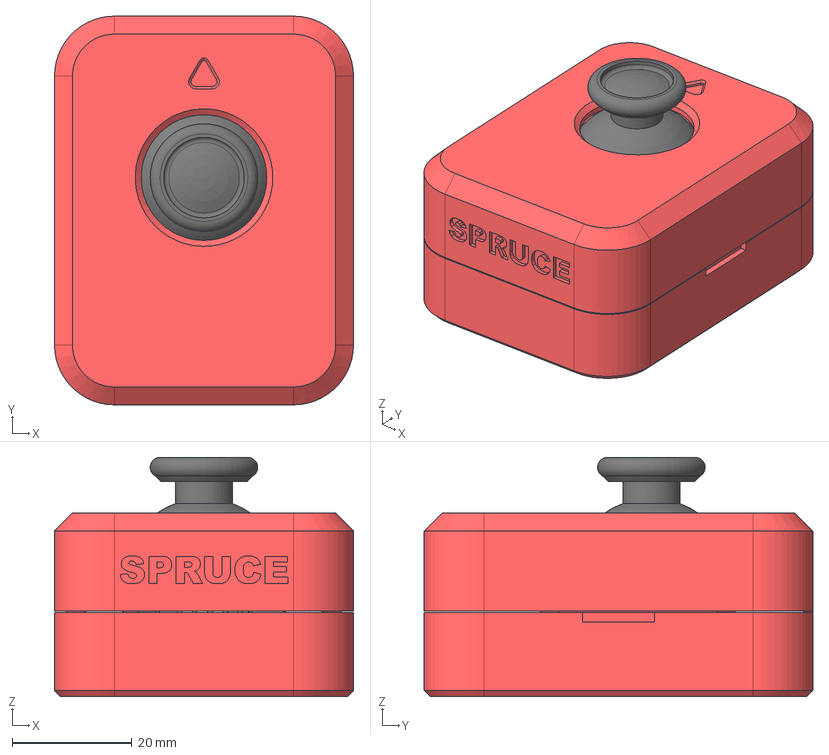
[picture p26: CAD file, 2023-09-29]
Design_Files/CAD_Design_Files/Spruce_Mini_Joystick.step
50.0 x 65.0 x 40.0 mm
shell bottom
shell top
Adafruit 512 Analog 2-axis Joystick v1
Cover
Male Header Right Angle 5 Pin

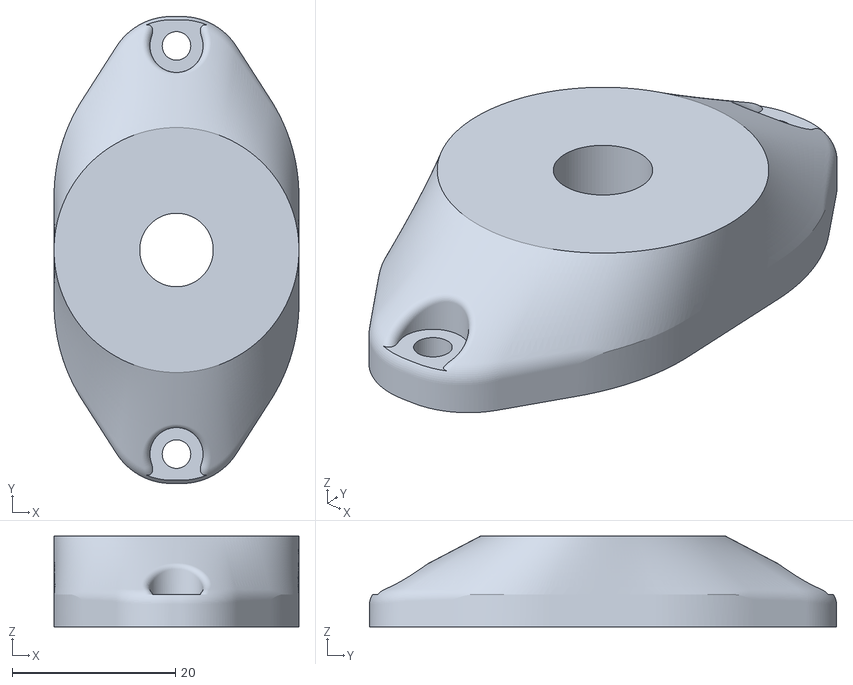
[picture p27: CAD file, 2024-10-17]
Build_Files/3D_Printing_Files/Joystick_Camera_Mount_Adapter.stl
30.0 x 57.2 x 11.1

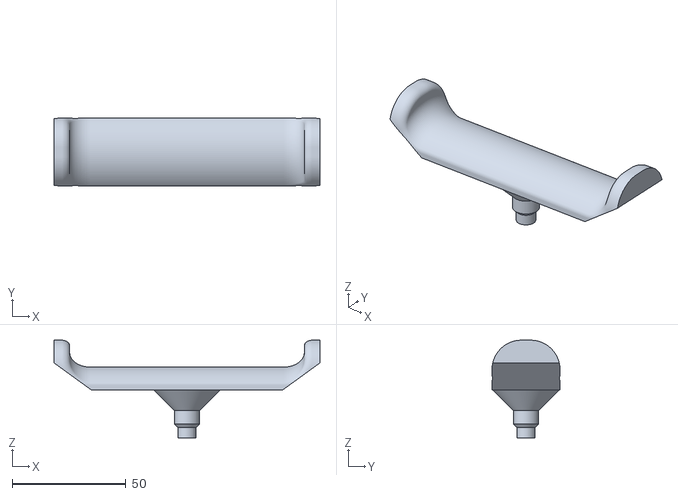
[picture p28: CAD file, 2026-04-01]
Build_Files/3D_Printing_Files/Toppers/Additional_Toppers/thumbstick-super-wide.stl
117.1 x 30.0 x 43.0

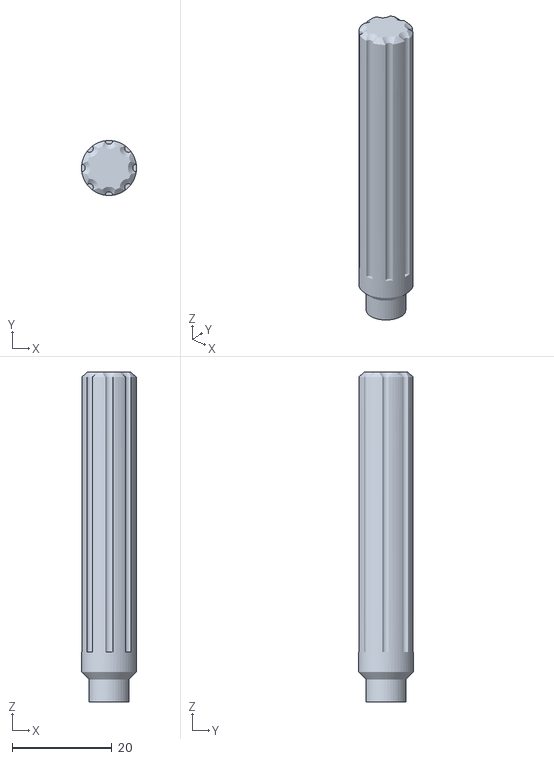
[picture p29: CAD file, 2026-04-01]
Build_Files/3D_Printing_Files/Toppers/Stick_Topper.stl
11.0 x 11.0 x 66.0

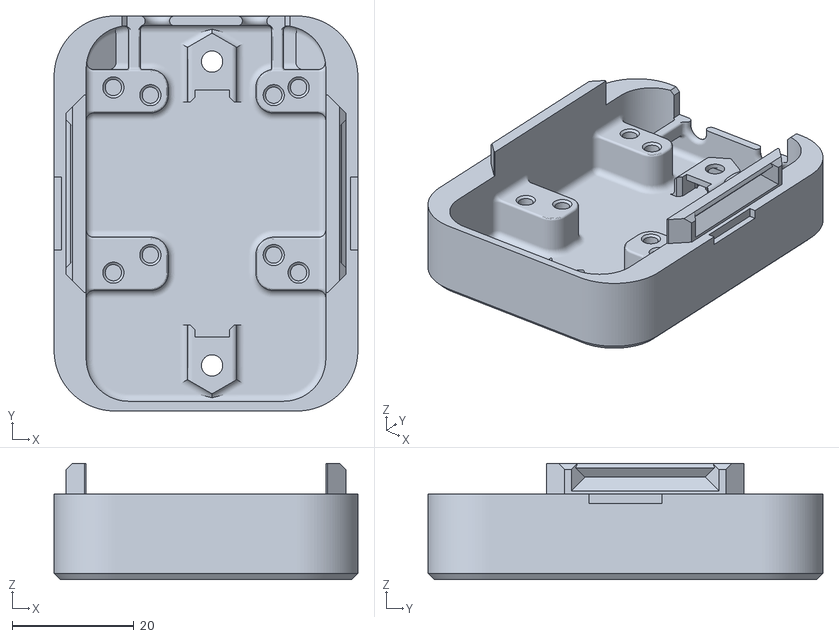
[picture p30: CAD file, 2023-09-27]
Build_Files/3D_Printing_Files/Spruce_enclosure_bottom.stl
50.0 x 65.0 x 19.1

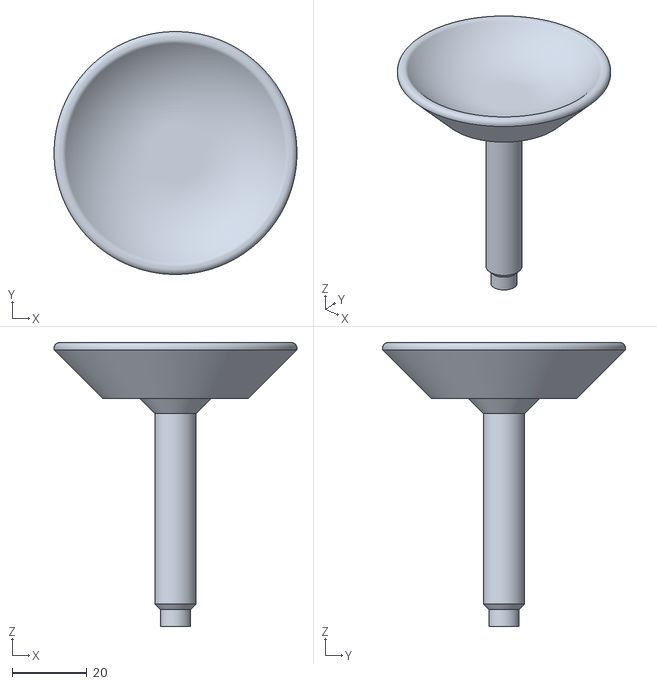
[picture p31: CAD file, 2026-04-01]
Build_Files/3D_Printing_Files/Toppers/Additional_Toppers/chin_cup.stl
65.0 x 65.0 x 76.0

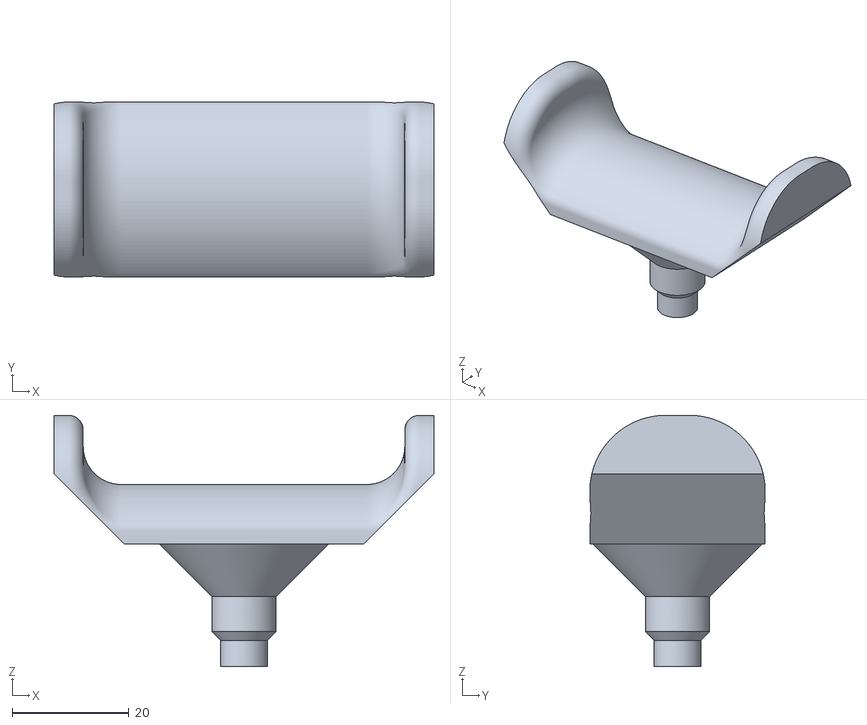
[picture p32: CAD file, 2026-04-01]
Build_Files/3D_Printing_Files/Toppers/Small_Goalpost_Topper.stl
65.0 x 30.0 x 43.0

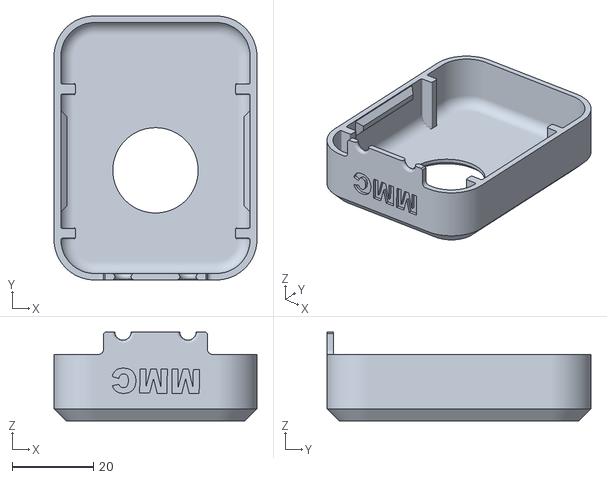
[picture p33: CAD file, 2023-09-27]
Build_Files/3D_Printing_Files/Spruce_enclosure_top.stl
50.0 x 65.0 x 21.9

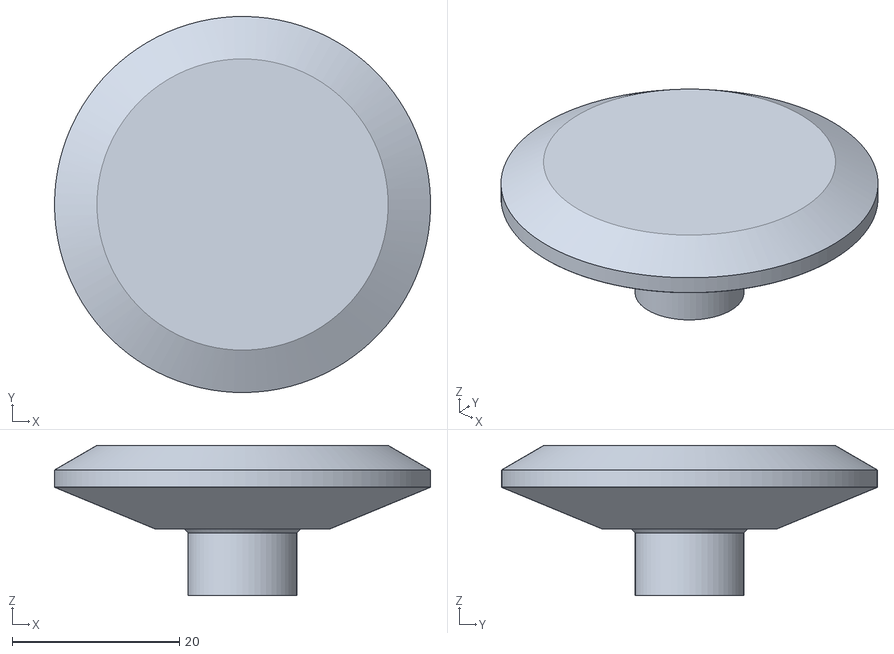
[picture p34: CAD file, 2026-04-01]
Build_Files/3D_Printing_Files/Toppers/Additional_Toppers/low-profile-dome-for-ps5.stl
45.0 x 45.0 x 18.0

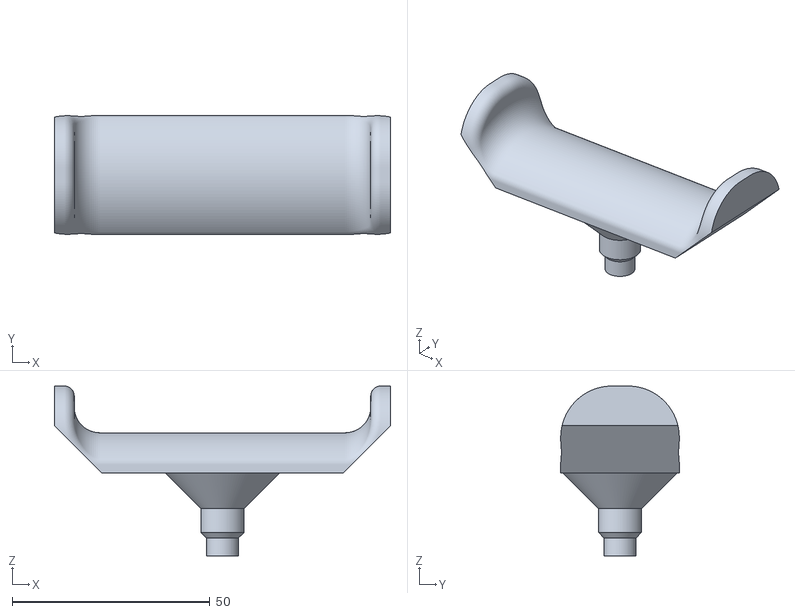
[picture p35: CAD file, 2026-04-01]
Build_Files/3D_Printing_Files/Toppers/Large_Goalpost_Topper.stl
85.0 x 30.0 x 43.0

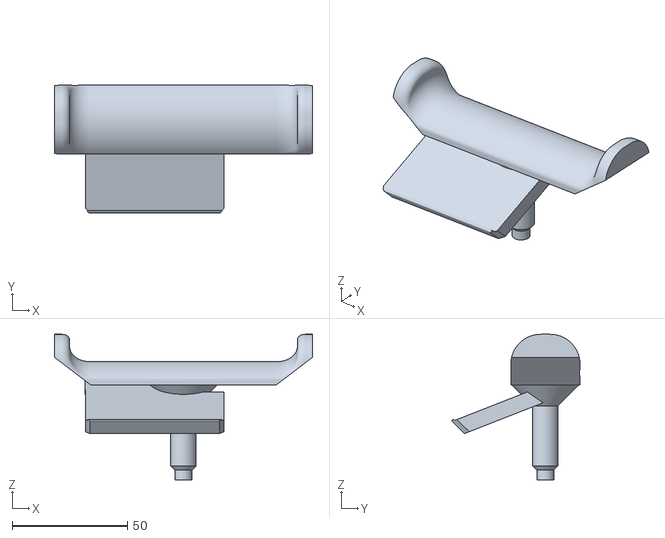
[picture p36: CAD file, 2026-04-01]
Build_Files/3D_Printing_Files/Toppers/Additional_Toppers/fps-super-wide.stl
111.7 x 55.5 x 63.0

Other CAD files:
Design_Files/CAD_Design_Files/Spruce Mini Joystick v13.step
Build_Files/3D_Printing_Files/Toppers/Concave_Topper.stl
Build_Files/3D_Printing_Files/Toppers/Additional_Toppers/fps.stl
Build_Files/3D_Printing_Files/Toppers/Convex_Topper.stl
Design_Files/CAD_Design_Files/Joystick RAM Mount Adapter v5.f3d
Design_Files/CAD_Design_Files/Joystick_Camera_Mount Narrow v3.f3d
Design_Files/CAD_Design_Files/Spruce_Mini_Joystick.f3z

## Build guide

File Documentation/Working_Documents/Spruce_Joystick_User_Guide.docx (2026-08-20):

## Introduction

The Spruce Mini Joystick is a small analog joystick compatible with the XAC or other analog input joystick devices, such as the Forest Joystick Mouse Hub. It has an included switch, that is activated by pressing down on the joystick topper.

## Features

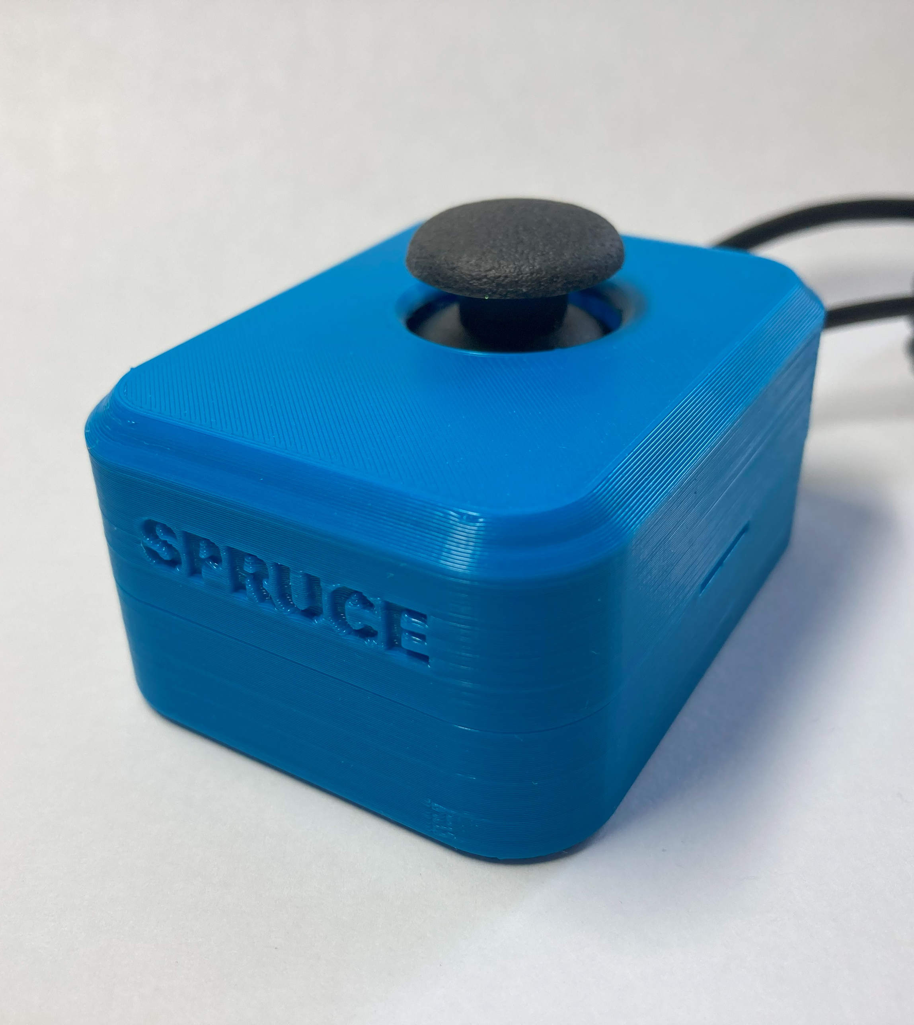
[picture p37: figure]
A photo of the Spruce Mini Joystick
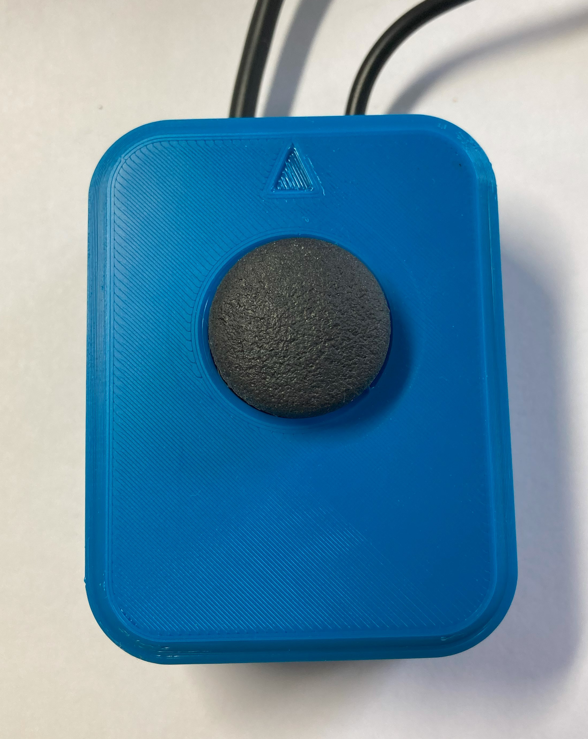
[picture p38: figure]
A photo of the Spruce Mini Joystick with red arrows f=pointing to important features.

Joystick and push switch

Arrow indicating “up” direction on joystick

Cable exit

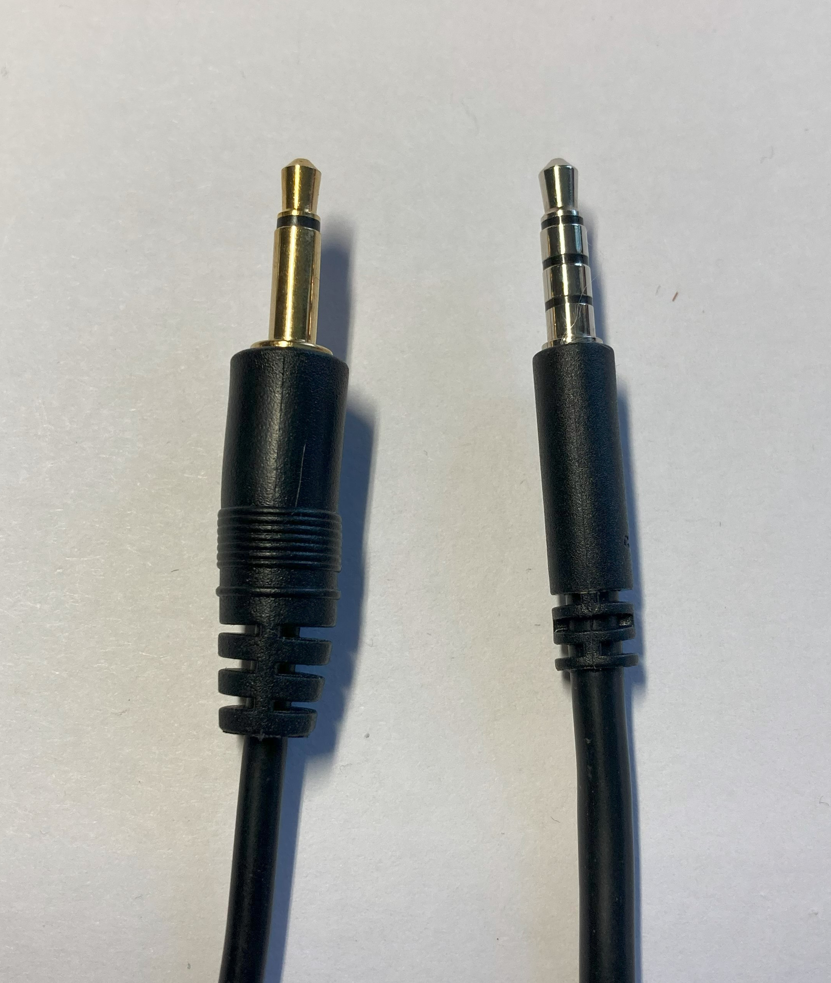
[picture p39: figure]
A mono audio cable and TRRS audio cable side by side.

Switch cable

(2 bands)

Joystick cable

(4 bands)

## Usage

### Using the Joystick Alone with Host Device

1. Plug the 3.5 mm TRRS cable (4 bands) from the joystick into the host device analog joystick input (such as the Xbox Adaptive Controller). If using the Xbox Adaptive Controller, plug it into X1 to use at the left joystick, or plug into X2 to use as the right joystick.
2. Ensure the arrow on the joystick is pointing in the “up/forward” direction, away from the user.
3. Mount the device if needed (see below).
4. Move joystick as you would with a standard controller (forward, left, backward, right).

### Using the Joystick and Push Switch with Host Device

1. Plug the switch cable (2 bands) into the desired switch input. If using the Xbox Adaptive Controller, this could be any port other than the X1 and X2 ports.
2. Plug the 3.5 mm TRRS cable (4 bands) from the joystick into the host device analog joystick input (such as the Xbox Adaptive Controller). If using the Xbox Adaptive Controller, plug it into X1 to use at the left joystick, or plug into X2 to use as the right joystick.
3. Ensure the arrow on the joystick is pointing in the “up/forward” direction, away from the user.
4. Mount the device if needed (see below).
5. Move joystick as you would with a standard controller (forward, left, backward, right).

Note: If using the Xbox Adaptive Controller (XAC), and using the push switch, make sure to plug in the switch cable before the joystick cable, or before moving the joystick. If the joystick was plugged in first and moved around, please power the XAC on and off before plugging in both the switch and joystick.

If the switch cable was previously plugged in, but now the joystick is being used alone, power the XAC off and on again.

### Compatibility

This device is compatible with the Xbox Adaptive Controller (XAC) (https://www.xbox.com/en-CA/accessories/controllers/xbox-adaptive-controller), PlayStation Access Controller (https://www.playstation.com/en-ca/accessories/access-controller/), Forest Hub (https://github.com/makersmakingchange/Forest-Joystick-Mouse-Hub), Enabled Controller (https://makersmakingchange.com/project/enabled-controller/), Enabled Controller Mini (https://www.makersmakingchange.com/s/product/enabled-controller-mini/01tJR0000006991YAA), and any other device that accepts a TRRS analog joystick input.

### Drift Troubleshooting

If you experience drift with the Spruce Mini Joystick when using with the Xbox Adaptive Controller:

1. Unplug the Xbox Adaptive Controller (XAC) if connected via USB.
2. Power the XAC off.
3. Plug the XAC back in if connecting via USB, or power on and connect via Bluetooth.
4. Move the joystick around in circles.

This process should resolve drift issues. Pay attention to the order that the joystick and switch cables are plugged in, if using the switch always plug it in first. If using the joystick alone do not plug in the switch.

### Mounting the Joystick

The Spruce Mini Joystick can be mounted using various methods, depending on your preference and how you can best access it. See the OpenAT Joystick Setup Guide (https://github.com/makersmakingchange/OpenAT-Joysticks/Resources/OpenAT_Joystick_Setup_Guide.pdf) for more information on different ways to mount the joystick.

A few options are:

1. Tabletop
  a. Alone
  b. With non-slip pads
  c. With hook and loop fasteners (such as Velcro)
2. Using a mount adapter
  a. Camera mount adapter used with camera mount, or any mount with ¼-20 threads

Note: The mounting options are shown on a different joystick but will apply the same to this one.

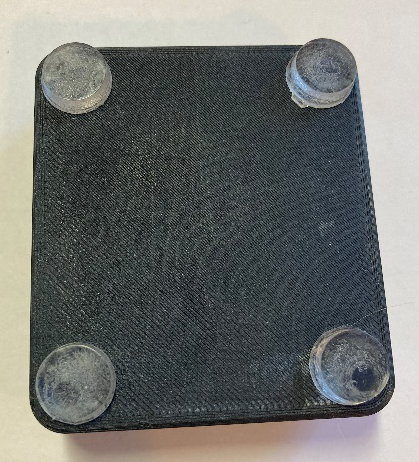
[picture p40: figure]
Bottom of the joystick with the no slip stoppers installed.
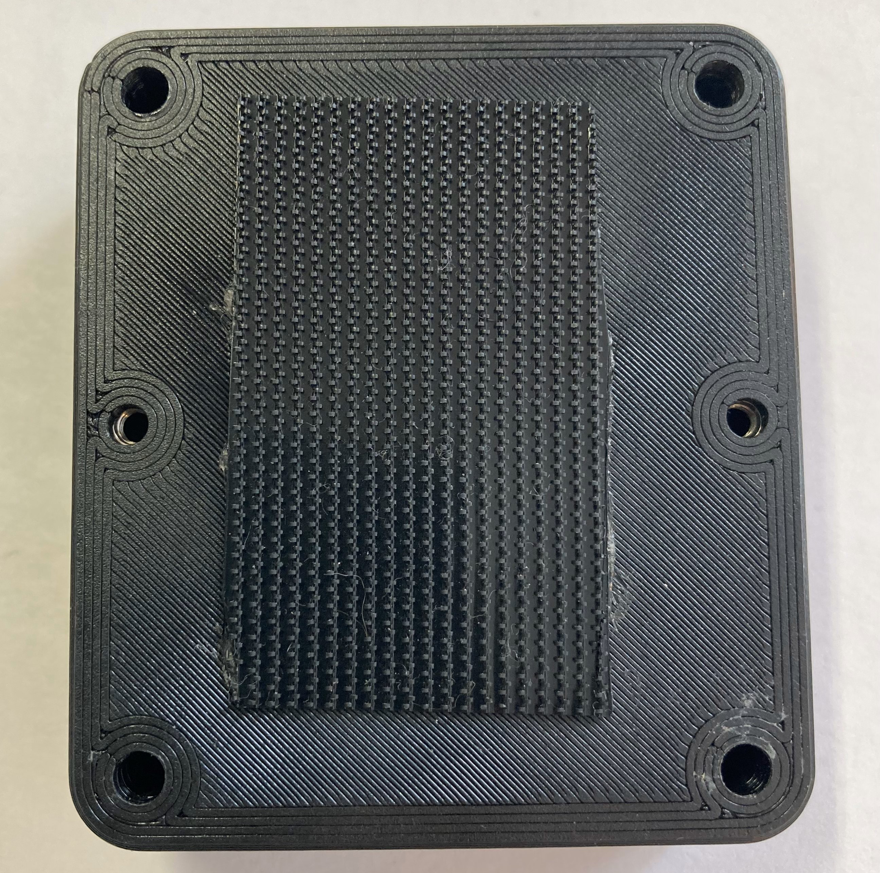
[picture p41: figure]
Bottom of the joystick with hook and loop fastener attached to the bottom. The hook side is shown stuck to the joystick.
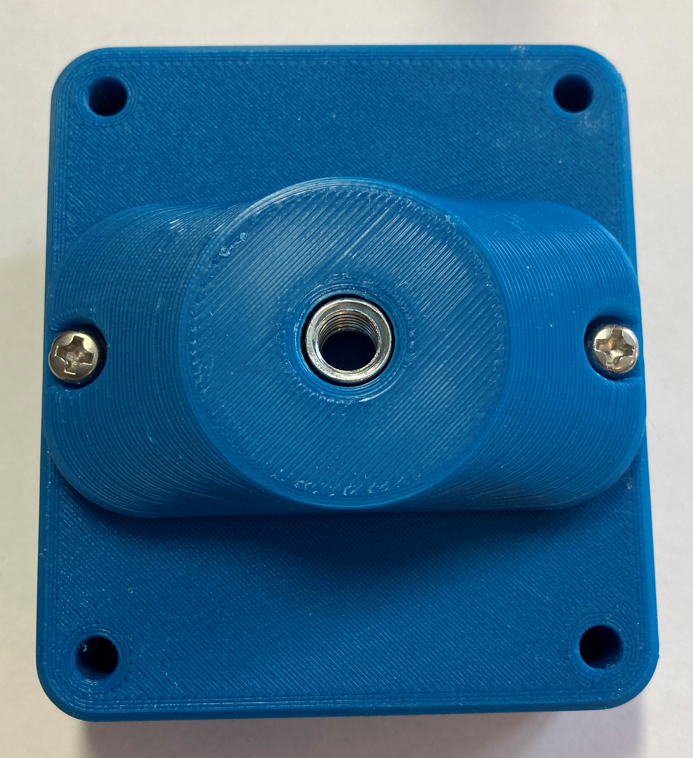
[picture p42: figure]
The camera mount adapter screwed into the bottom of the Birch Mini Joystick, using two small screws. Both the camera mount adapter and the joystick are light blue. The screws are circled in red.

### Changing Toppers

The Spruce Joystick comes with a standard rubber like small dome topper like shown in the feature photo above. There are various 3D printed toppers that are available for the Spruce Joystick that can replace the standard topper. Such as the following:

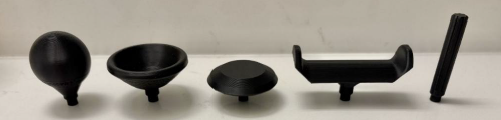
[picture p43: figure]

To add a 3D printed topper on the Spruce, follow these instructions:

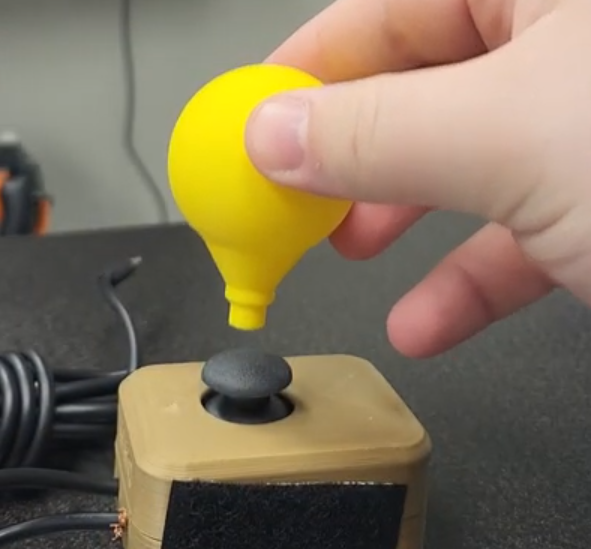
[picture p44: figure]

1. We will replace the standard black small dome topper with a 3D printed topper.

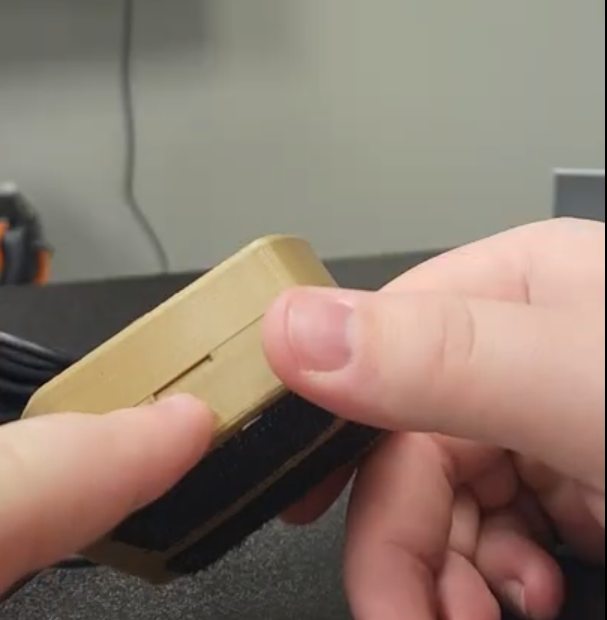
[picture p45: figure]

2. First, locate the small slits on the side of the Spruce Joystick. This is where the top and bottom pieces of the Spruce Joystick join.

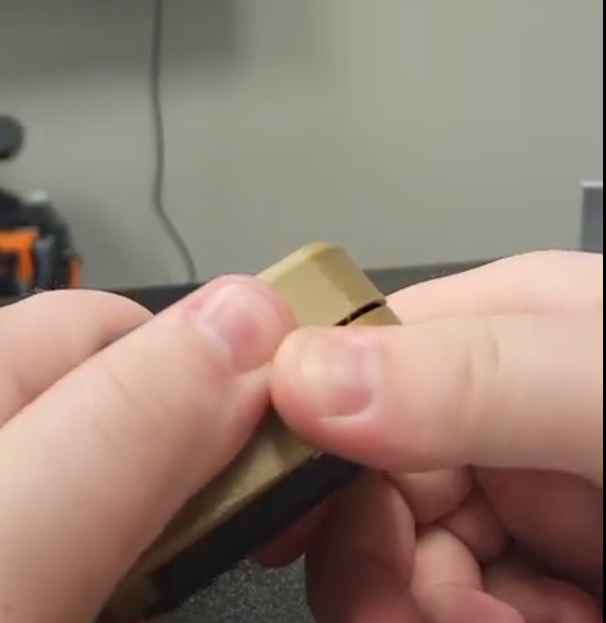
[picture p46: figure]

3. Hold the bottom half of the Spruce Joystick and press/pull the top half off. Note: there are no screws holding the top and bottom half of the enclosure together, they just snap together.

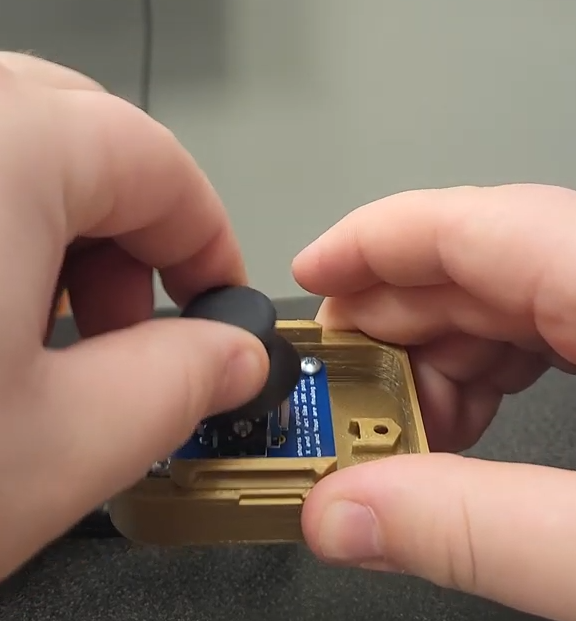
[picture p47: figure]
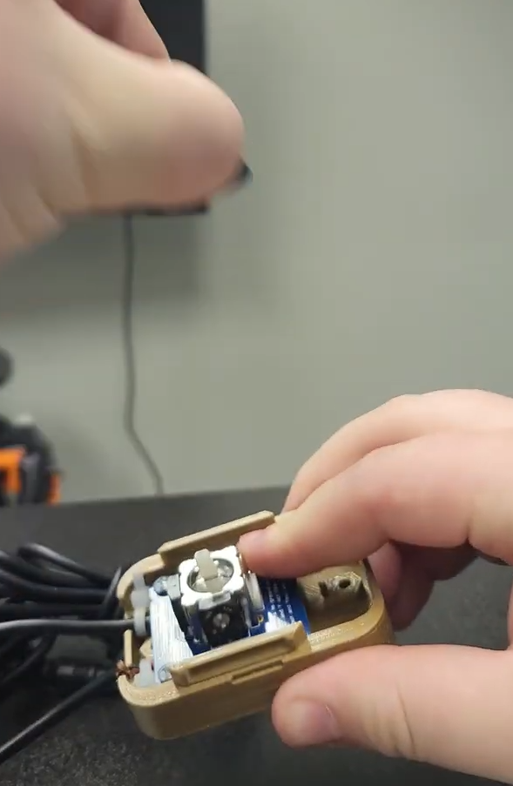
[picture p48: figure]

4. You now have the two halves of the joystick enclosure separated. You can remove the standard topper by pulling straight up. Note: the topper may have come off with the top half in step 3.

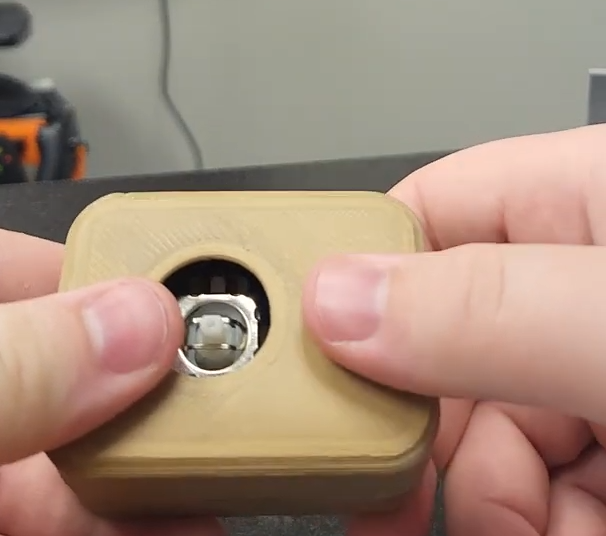
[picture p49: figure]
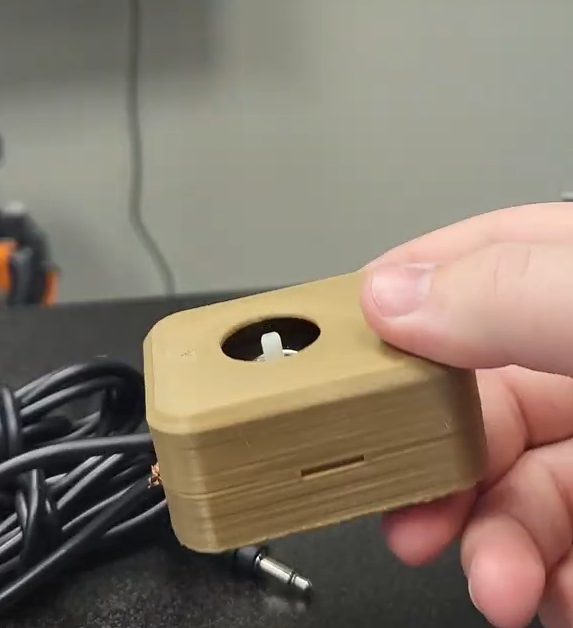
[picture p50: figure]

5. Line up the top half of the Spruce Joystick enclosure back onto the bottom half and press them together. Make sure the arrow on the top half is pointing towards the cables.

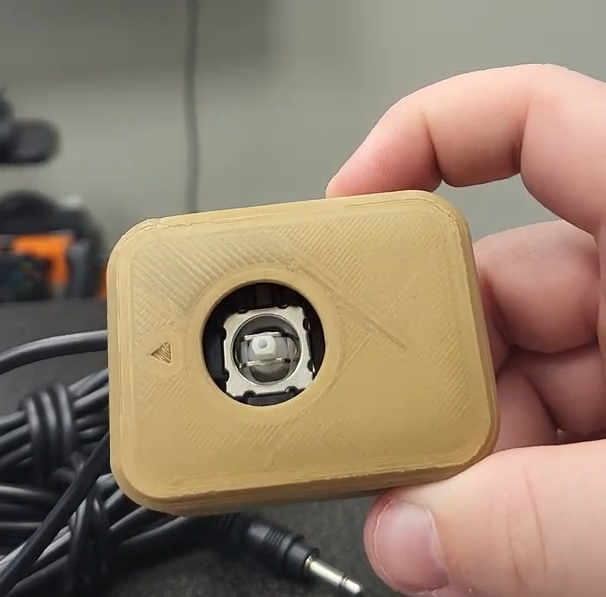
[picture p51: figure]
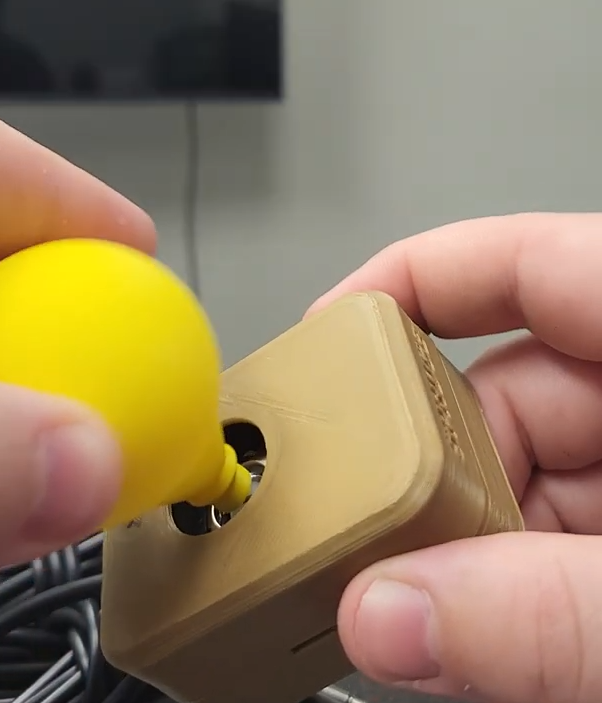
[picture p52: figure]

6. Now, take your 3D printed topper and line up the rectangular slot on it with the white rectangular peg on the joystick and press them together.

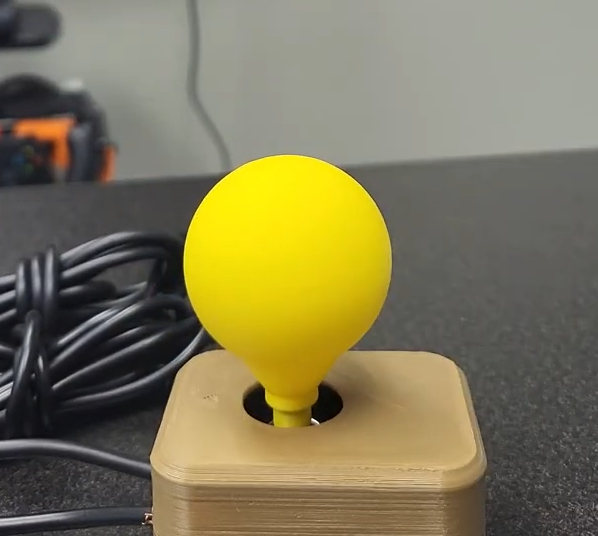
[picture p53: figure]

7. You have now added a 3D printed topper. To swap 3D printed toppers, simply pull off the topper and press on a new one. Note: You can put the standard topper back on by following these steps in reverse.

## Specifications

Joystick Range of Motion | ± 30°
Joystick Range of Motion at Tip of Default Topper | ± 15 mm
Joystick Activation Force at Tip of Default Topper | 75 grams
Total Height with Default Topper | 40 mm
Enclosure Height | 31 mm
Enclosure Width | 50 mm
Enclosure Length | 65 mm
Weight (including cables) | 108 grams

## Cleaning

Wipe the outside of the device with a lukewarm, damp cloth. Do not use hot water on this device or the plastic housing may warp. Do not submerge the device.

© 2023 by Neil Squire Society. This work is licensed under the CC BY SA 4.0 License: http://creativecommons.org/licenses/by-sa/4.0 Files available at https://github.com/makersmakingchange/Spruce-Mini-Joystick Page 2 of 3

V1.0.2 | August 2026 Spruce Mini Joystick user Quick Guide

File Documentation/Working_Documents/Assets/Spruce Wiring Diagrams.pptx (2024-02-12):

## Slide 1

Mono cable

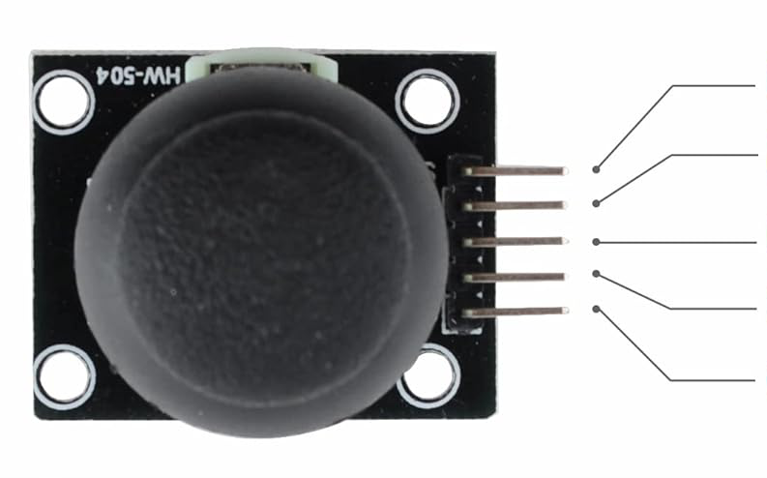
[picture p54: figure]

Sleeve

Tip

SW

VRY

TRRS audio cable

VRX

+5V

Sleeve

GND

Ring 2

Ring 1

Tip

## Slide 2

TRRS audio cable

Sleeve

Ring 2

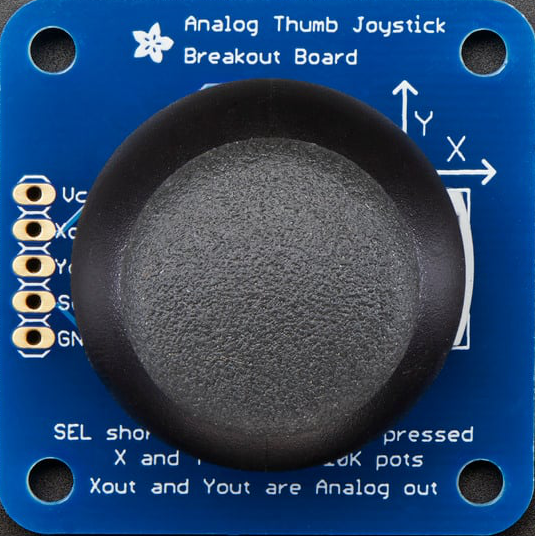
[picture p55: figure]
Top down showing thumbstick cap

Ring 1

Tip

VCC

X out

Y out

Tip

Sel

Sleeve

GND

Mono cable

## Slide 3

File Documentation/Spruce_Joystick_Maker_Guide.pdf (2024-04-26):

V1.1 | APRIL 2024

## Spruce Mini Joystick

## MAKER GUIDE

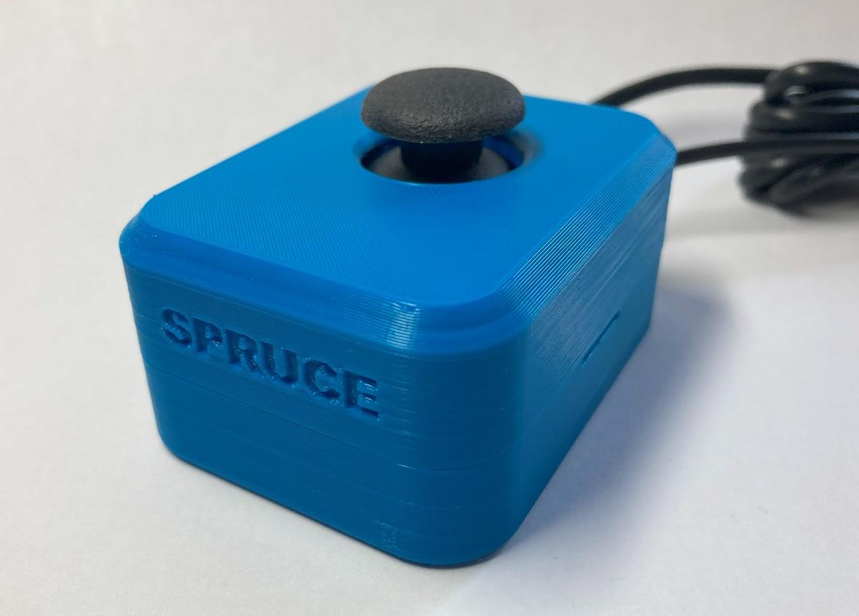
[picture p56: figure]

© 2023 Neil Squire Society. (https://www.neilsquire.ca/) This documentation is licensed under the CC BY SA 4.0 License: http://creativecommons.org/licenses/by-sa/4.0
Files available at https://github.com/makersmakingchange/Spruce-Mini-Joystick | Page 1 of 34

Overview
This document contains the necessary information to build the device.

## MAKER GUIDE

Files available at https://github.com/makersmakingchange/Spruce-Mini-Joystick | Page 2 of 34

Contents
Overview | 1
Maker Checklist | 4
Maker To Do List | 4
Items to Give to User | 4
Tool List | 5
Customization Guide | 6
Joystick | 6
Toppers | 6
Mounting | 6
3D Printing Guide | 7
3D Printing Summary | 7
3D Printing Settings | 7
Spruce Mini Joystick Enclosure - Single Unit | 7
Post-Processing | 7
Examples of Quality Prints | 7
Spruce_enclosure_bottom.stl | 7
Spruce_enclosure_top.stl | 8
Assembly Guide | 9
Spruce Mini Joystick Assembly – Adafruit PS2 Joystick | 10
Required Components | 10
Tools and Personal Protective Equipment (PPE) | 10
Required Tools | 10
Optional Tools | 10
Required Personal Protective Equipment (PPE) | 10
Assembly Steps – Adafruit Joystick | 11
Spruce Mini Joystick Assembly – Generic PS2 Joystick | 21
Required Components | 21
Tools and Personal Protective Equipment (PPE) | 21
Required Tools | 21

## MAKER GUIDE

Files available at https://github.com/makersmakingchange/Spruce-Mini-Joystick | Page 3 of 34
Optional Tools | 21
Required Personal Protective Equipment (PPE) | 21
Assembly Steps – Generic PS2 Joystick | 22
Testing | 32
Testing using a Multimeter | 32
Test 1: Testing for Short Circuits | 32
Test 2: Testing Vertical Joystick Axis | 32
Test 3: Testing Horizontal Joystick Axis | 33
Test 4: Testing Push Button | 34
Testing using an USB-HID Gamepad Device | 34

## MAKER GUIDE

Files available at https://github.com/makersmakingchange/Spruce-Mini-Joystick | Page 4 of 34

Maker Checklist
This list provides an overview of the steps required to build and deliver the device.

Maker To Do List
Read through the Maker Guide to become familiar with required components, tools, supplies, and safety gear and overall assembly steps.
Talk to User about customization options (e.g., colour, any special requests, etc.)
- Enclosure Colour
- Joystick Toppers
- Mounting Options
- USB Interfaces (e.g., Forest Hub) Order hardware components
3D print all 3D printed components.
Gather tools, supplies, and safety equipment. Assemble the device.
Test device.
Print “User Guide”

Items to Give to User
Assembled, tested joystick Joystick toppers (if requested) Mounting Adapters (if requested) “User Guide”

## MAKER GUIDE

Files available at https://github.com/makersmakingchange/Spruce-Mini-Joystick | Page 5 of 34

Tool List
- Flush Cutters
- Wire Strippers
- #3 Philips Head Screwdriver
- Pliers
- Soldering Iron and Solder
- Multimeter

## MAKER GUIDE

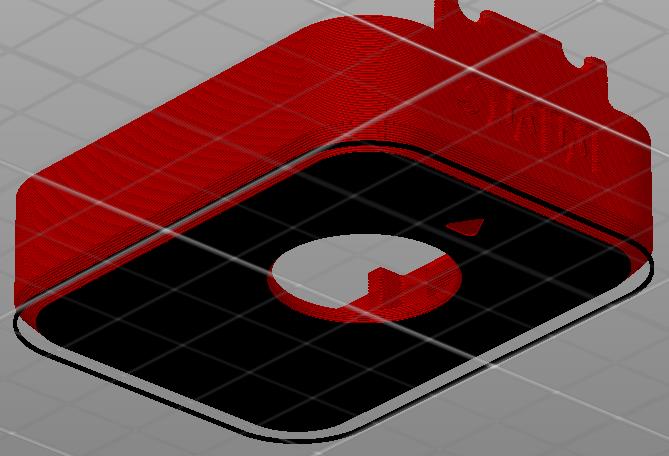
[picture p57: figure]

Files available at https://github.com/makersmakingchange/Spruce-Mini-Joystick | Page 6 of 34

Customization Guide

Joystick
The enclosure can be printed in the user’s desired colour. Using a colour swap after the first few layers can help to make the Up/Forward arrow stand out more.

Toppers
3D printed joystick toppers can be added to the joystick.

Any PS2 style thumbstick toppers will work here, one example is this set of toppers designed by AbleGamers¹
. (https://www.printables.com/model/501869-analog-thumbstick-topper-collection)

Mounting
Mount adapters can be added for custom mounting solutions.

1 https://www.printables.com/model/501869-analog-thumbstick-topper-collection

## MAKER GUIDE

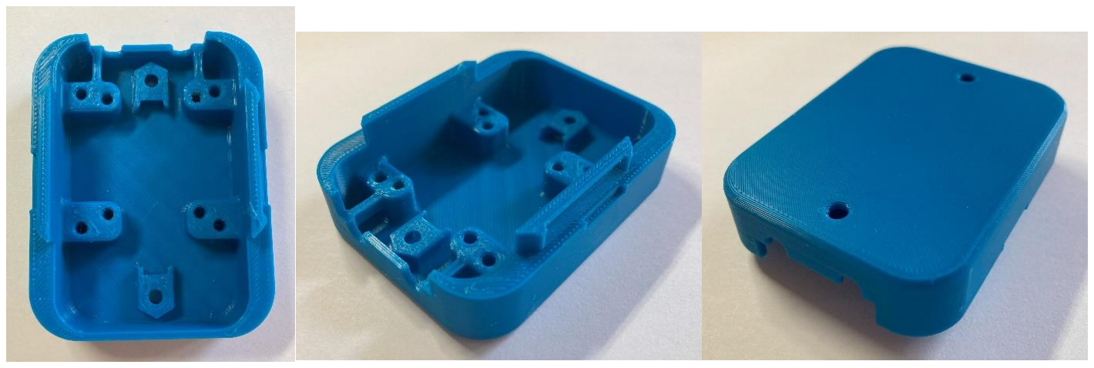
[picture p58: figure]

Files available at https://github.com/makersmakingchange/Spruce-Mini-Joystick | Page 7 of 34

3D Printing Guide

3D Printing Summary
Metrics | Single Unit
Total Print Time (min) | 3h08m
Total Number of Components | 2
Typical Total Mass (g) | 28
Typical Number of Print Setups | 1

3D Printing Settings

Spruce Mini Joystick Enclosure - Single Unit
Print File Name | Qty | Total Print Time (hr:min) | Mass (g) | Infill (%) | Support (Y/N) | Layer Height/ Nozzle Diameter(mm) | Notes
Spruce_enclosure_ bottom.stl | 1 | 1:46 | 16 | 20 | N | 0.2/0.4 | Print in given orientation
Spruce_enclosure_ top.stl | 1 | 1:22 | 12 | 20 | N | 0.2/0.4 | Print in given orientation

Post-Processing
- Remove any stringing or blobs

Examples of Quality Prints

Spruce_enclosure_bottom.stl

## MAKER GUIDE

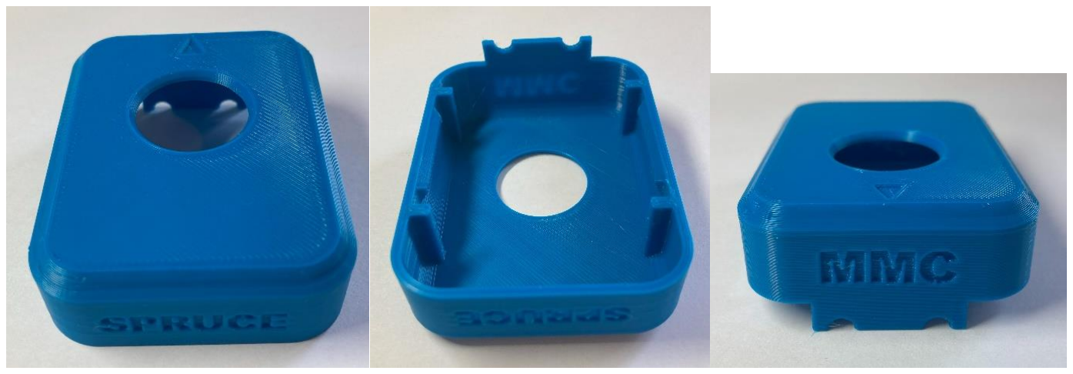
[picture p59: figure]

Files available at https://github.com/makersmakingchange/Spruce-Mini-Joystick | Page 8 of 34

Spruce_enclosure_top.stl

## MAKER GUIDE

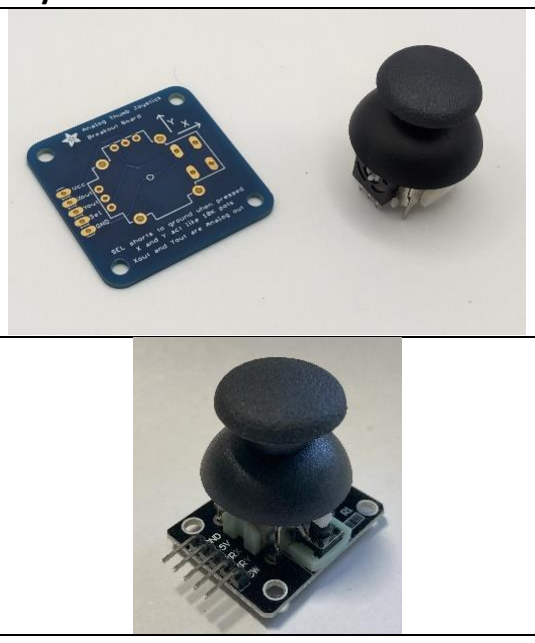
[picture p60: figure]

Files available at https://github.com/makersmakingchange/Spruce-Mini-Joystick | Page 9 of 34

Assembly Guide
Follow the instructions that correspond to the joystick module that you have.
Joystick Module | Assembly Instructions
| Spruce Mini Joystick Assembly – Adafruit PS2 Joystick– Page 10
| Spruce Mini Joystick Assembly – Generic PS2 Joystick – Page 21

## MAKER GUIDE

Files available at https://github.com/makersmakingchange/Spruce-Mini-Joystick | Page 10 of 34

Spruce Mini Joystick Assembly – Adafruit PS2 Joystick

Required Components
1

Adafruit PS2
Joystick | QTY 1 | 2

TRRS Audio
Cable | QTY 1 | 3 | Mono cable | QTY 1
4 | 4” cable tie | QTY 2 | 5

#4 3/8” Screws,

self threading | QTY 4 | 6 | M3 Hex Nuts | QTY 2

7

3D Printed
Enclosure Bottom | QTY 1 | 8

3D Printed
Enclosure Top QTY 1

Tools and Personal Protective Equipment (PPE)

Required Tools
- Flush Cutters
- Wire Strippers
- #3 Philips Screwdriver
- Pliers
- Soldering Iron and
Solder
- Multimeter

Optional Tools
- Electrical Continuity
Tester (e.g.,
Multimeter)

Required Personal Protective Equipment (PPE)
- Safety Goggles

## MAKER GUIDE

Files available at https://github.com/makersmakingchange/Spruce-Mini-Joystick | Page 11 of 34

Assembly Steps – Adafruit Joystick

Step 1: Prepare Audio Cable
If you are using the pre-prepared TRRS cable from DigiKey, pictured in the component list, you can skip this step.

If using a different cable, prepare the wires for soldering:
- Cut the TRRS cable to length (typically 1 m).
- Strip off approximately 2 cm of the outer insulation.
- Then, separate the 4 individual inner wires. If there are three insulated wires plus copper strands, twist these copper strands together to be one of your wires. If there are 4 insulated wires plus loose copper stranded wires, cut off these copper wires.
- Strip off approximately 0.5 cm of insulation from the inner wires.
- For each inner wire, twist the inner strands together
Step 2: Identify Audio Cable Wires

If using the pre-prepared DigiKey cable, you can skip this step.

You should use a multimeter or other continuity tester to confirm which wire corresponds to which part of the plug. Follow this guide for checking continuity (https://www.youtube.com/watch?v=T4p8UQZqh5U) to determine which wire corresponds to the Sleeve, Ring 1, Ring 2, and Tip of the TRRS cable plug.

TRRS Plug | DigiKey TRRS cable | Your TRRS cable
Sleeve | Black
Ring 2 | Green
Ring 1 | White
Tip | Red

## MAKER GUIDE

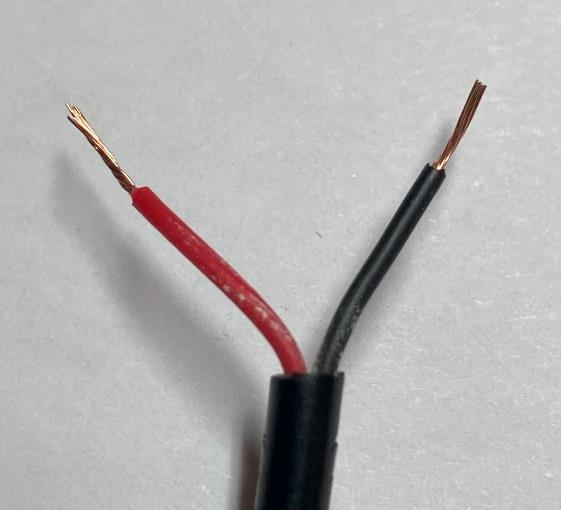
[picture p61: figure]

Files available at https://github.com/makersmakingchange/Spruce-Mini-Joystick | Page 12 of 34
Step 3: Prepare Mono Cable
If you are using the pre-prepared mono cable from DigiKey, pictured in the component list, skip this step.

If using a different cable, you’ll need to prepare the wires for soldering:
- Cut the mono cable to length (typically 1 m).
- Strip off approximately 2 cm of the outer insulation.
- Then, separate the 2 individual inner wires. If there is one insulated wire plus copper strands, twist these copper strands together to be one of your wires.
- Strip off approximately 0.5 cm of insulation from the inner wires.
- For each inner wire, twist the inner strands together
Step 4: Identify Mono Cable Wires
If using the pre-prepared DigiKey cable, you can skip this step.

You should use a multimeter or other continuity tester to confirm which wire corresponds to which part of the plug. Follow this guide for checking continuity (https://www.youtube.com/watch?v=T4p8UQZqh5U) to determine which wire corresponds to the Sleeve, and Tip of the mono cable plug.

Mono Plug | DigiKey mono cable | Your mono cable
Tip | Red
Sleeve | White

## MAKER GUIDE

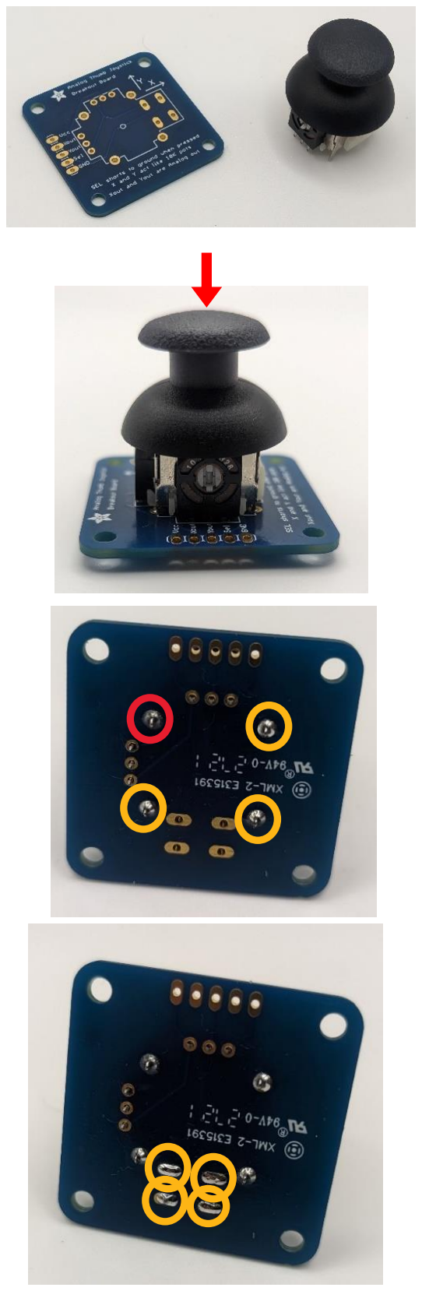
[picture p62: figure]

Files available at https://github.com/makersmakingchange/Spruce-Mini-Joystick | Page 13 of 34
Step 5: Insert Joystick into Breakout Board and Solder

The Adafruit Joystick needs to be soldered to the Joystick breakout board before it is ready for use.

Carefully insert the joystick module into the joystick breakout board, ensuring all pins are inserted and the joystick is sitting flat.

Solder one (1) of the main joystick lugs. Ensure the joystick is flat against the breakout board, and then solder the remaining three (3) main lugs.

Solder the four (4) lead for the joystick switch.

## MAKER GUIDE

Files available at https://github.com/makersmakingchange/Spruce-Mini-Joystick | Page 14 of 34

Solder the three (3) leads for the X-axis potentiometer and three (3) leads for the Y-axis potentiometer.

The prepared joystick module.

## MAKER GUIDE

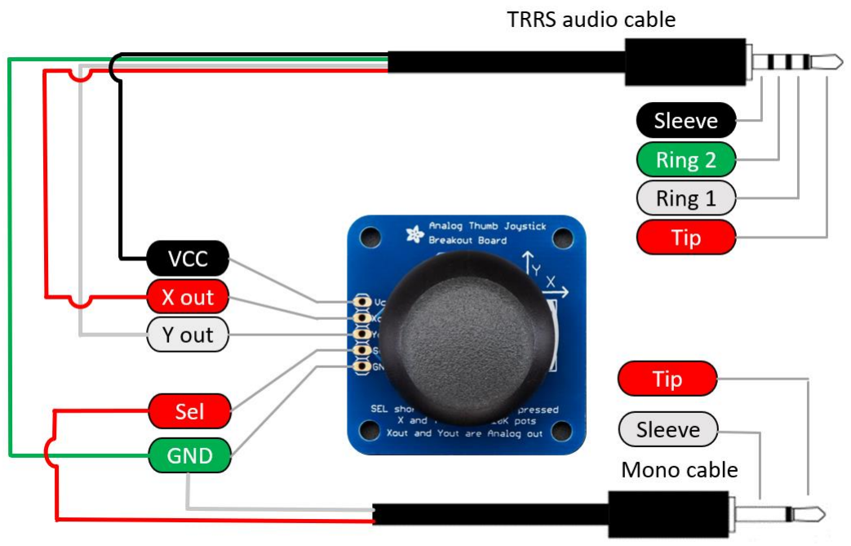
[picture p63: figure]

Files available at https://github.com/makersmakingchange/Spruce-Mini-Joystick | Page 15 of 34

Adafruit Joystick Wiring diagram

JOYSTICK BOARD Label | TRRS Plug | DigiKey TRRS Cable | Your TRRS CABLE | Mono PLUG | DigiKey Mono CABLE | Your Mono Cable
Vcc | Sleeve | Black | | --- | --- | ---
Xout | Tip | Red | | --- | --- | ---
Yout | Ring 1 | White | | --- | --- | ---
Sel | --- | --- | --- | Tip | Red
GND | Ring 2 | Green | | Sleeve | White

## MAKER GUIDE

Files available at https://github.com/makersmakingchange/Spruce-Mini-Joystick | Page 16 of 34
Step 6: Solder TRRS Sleeve to Voltage (Vcc) Pad

Insert the TRRS audio cable sleeve wire (black) into Vcc pad on the joystick breakout, with the wire going in from the bottom of the board to the top.

Solder the wire to the pad on the top of the board.

Step 7: Solder TRRS Tip to X (Xout) Pad

Insert the TRRS audio cable tip wire (red) into the Xout pad on the joystick breakout, with the wire going in from the bottom of the board to the top.

Solder the wire to the pad on the top of the board.

Step 8: Solder TRRS R1 to Y (Yout) Pad

Insert the TRRS audio cable ring 1 wire (white) into the Yout pad on the joystick breakout, with the wire going in from the bottom of the board to the top.

Solder the wire to the pad on the top of the board.

## MAKER GUIDE

Files available at https://github.com/makersmakingchange/Spruce-Mini-Joystick | Page 17 of 34
Step 9: Solder Mono Cable Tip to Switch (SW) Pad

Insert the Mono audio cable tip wire (red) into the Sel pad on the joystick breakout, with the wire going in from the bottom of the board to the top.

Solder the wire to the pad on the top of the board.

Step 10: Solder Mono Cable Sleeve and TRRS Cable R2 to Ground (GND) Pad

Take both the mono audio cable sleeve wire (white) and the TRRS audio cable Ring 2 wire (green) and twist together and insert into the GND pad on the joystick breakout, going from the bottom of the board to the top.

Solder the wires to the pads on the top of the board.

Step 11: Clean up Wires

Use flush cutters to trim any excess wires from the soldered pads.

## MAKER GUIDE

Files available at https://github.com/makersmakingchange/Spruce-Mini-Joystick | Page 18 of 34
Step 12: Check for Shorts
Inspect the board and check that none of the connections are shorted.

There should be no
bridges/connections between adjacent pins.

If you have a multimeter, you can
use it to double check continuity.
Step 13: Insert M3 Hex Nuts into Enclosure Bottom

Take the enclosure bottom
and insert the M3 nuts into
the slots as shown. You may
require a tool such as
needle-nosed pliers or a
screwdriver to push the
nuts into place.
Step 14: Position Joystick Unit

Thread the two cables from the joystick unit out the two cutouts at the back of the enclosure.

Ensure that the cables go between the screw holes and the captive nut piece and won’t interfere with screwing down the joystick.

## MAKER GUIDE

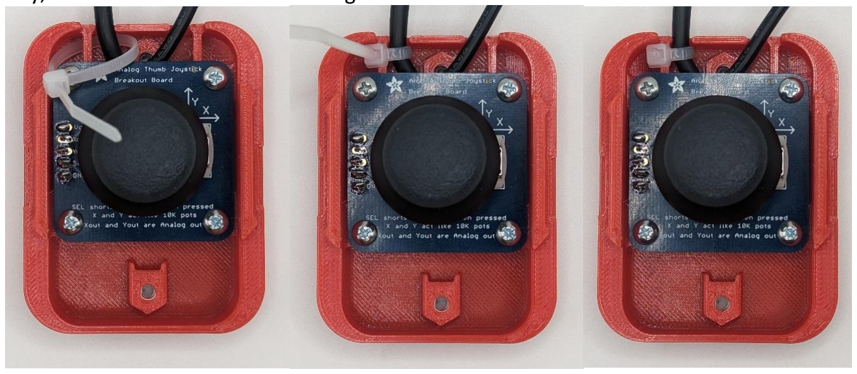
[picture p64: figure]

Files available at https://github.com/makersmakingchange/Spruce-Mini-Joystick | Page 19 of 34
Step 15: Screw in joystick unit
Position the joystick unit over the screw holes, with the cables running underneath. There are two (2) sets of screw holes for two different joystick units, find the set that matches your joystick.

Check the orientation of the joystick, and make sure that it matches the photo. The text on the board should be upright when the cables are coming out of the case away from you.

Screw in all four (4) screws through the joystick unit and
enclosure. Be careful not to over tighten.
Step 16: Fasten First Cable Tie
Thread the cable tie under the left cable and the 3D printed beam, going from the middle towards the edge.

Tighten the cable tie as much as you are able with your hands. The cable should now feel secure and unable to wiggle around.

Lastly, cut off the excess cable tie using flush cutters.

## MAKER GUIDE

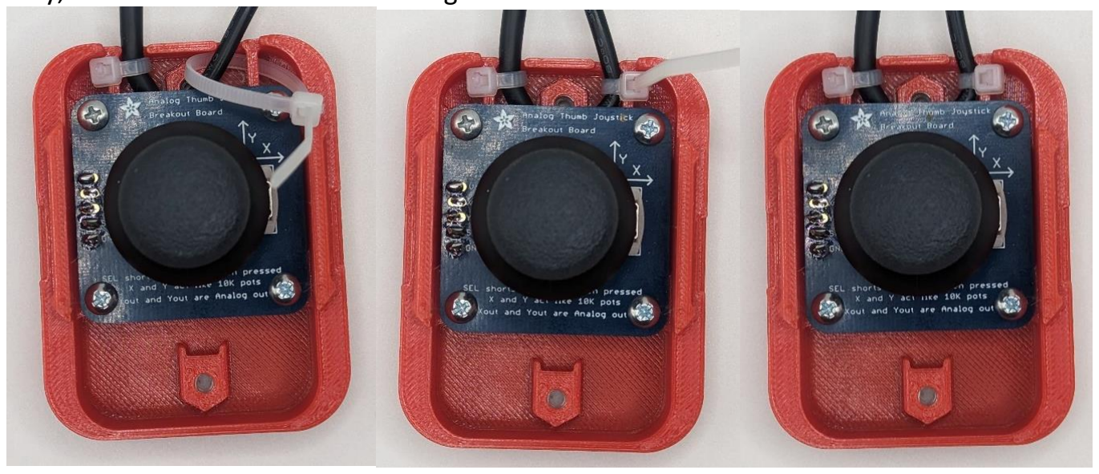
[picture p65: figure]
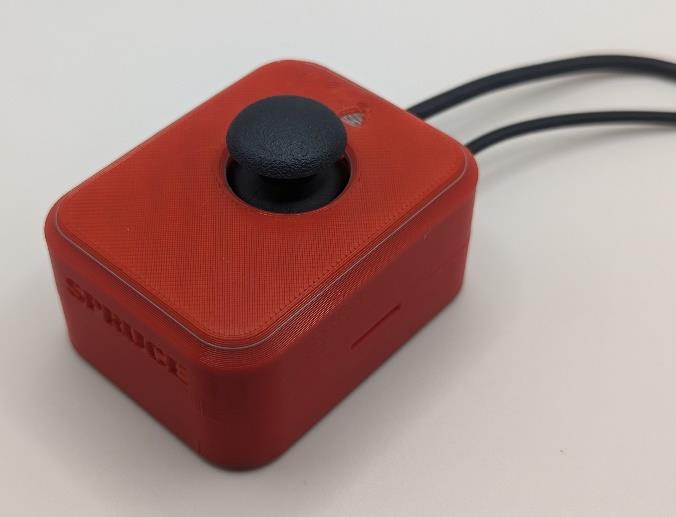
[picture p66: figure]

Files available at https://github.com/makersmakingchange/Spruce-Mini-Joystick | Page 20 of 34
Step 17: Fasten Second Cable Tie
Repeat with the second cable tie, thread the cable tie under the left cable and the 3D printed beam, going from the middle towards the edge.

Tighten the cable tie as much as you are able with your hands. The cable should now feel secure and unable to wiggle around.

Lastly, cut off the excess cable tie using flush cutters.

Step 18: Assemble Enclosure

Line up the enclosure top and apply downward pressure to snap it into place.

Proceed to Testing.

## MAKER GUIDE

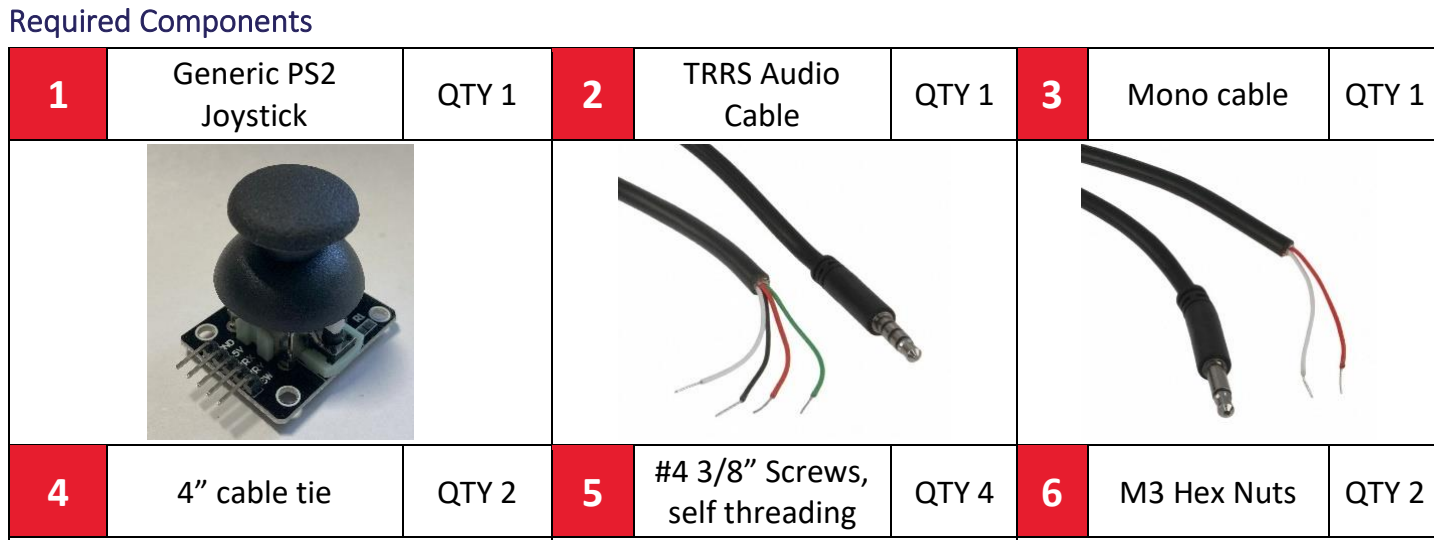
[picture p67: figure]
Required Components; Generic PS2; Joystick; QTY 1; TRRS Audio; Cable; Mono cable; 4” cable tie; QTY 2; #4 3/8” Screws,; self threading; QTY 4; M3 Hex Nuts

Files available at https://github.com/makersmakingchange/Spruce-Mini-Joystick | Page 21 of 34

Spruce Mini Joystick Assembly – Generic PS2 Joystick

7

3D Printed
Enclosure Bottom | QTY 1 | 8

3D Printed
Enclosure Top QTY 1

Tools and Personal Protective Equipment (PPE)

Required Tools
- Flush Cutters
- Wire Strippers
- #3 Philips Screwdriver
- Pliers
- Soldering Iron and
Solder
- Multimeter

Optional Tools
- Electrical Continuity
Tester (e.g.,
Multimeter)

Required Personal Protective Equipment (PPE)
- Safety Goggles

## MAKER GUIDE

Files available at https://github.com/makersmakingchange/Spruce-Mini-Joystick | Page 22 of 34

Assembly Steps – Generic PS2 Joystick

Step 1: Prepare Audio Cable
If you are using the pre-prepared TRRS cable from DigiKey, pictured in the component list, you can skip this step.

If using a different cable, prepare the wires for soldering:
- Cut the TRRS cable to length (typically 1 m).
- Strip off approximately 2 cm of the outer insulation.
- Then, separate the 4 individual inner wires. If there are three insulated wires plus copper strands, twist these copper strands together to be one of your wires. If there are 4 insulated wires plus loose copper stranded wires, cut off these copper wires.
- Strip off approximately 0.5 cm of insulation from the inner wires.
- For each inner wire, twist the inner strands together
Step 2: Identify Audio Cable Wires

If using the pre-prepared DigiKey cable, you can skip this step.

You should use a multimeter or other continuity tester to confirm which wire corresponds to which part of the plug. Follow this guide for checking continuity (https://www.youtube.com/watch?v=T4p8UQZqh5U) to determine which wire corresponds to the Sleeve, Ring 1, Ring 2, and Tip of the TRRS cable plug.

TRRS PLUG | DIGIKEY TRRS CABLE | YOUR TRRS CABLE
SLEEVE | Black
RING 2 | Green
RING 1 | White
TIP | Red

## MAKER GUIDE

Files available at https://github.com/makersmakingchange/Spruce-Mini-Joystick | Page 23 of 34
Step 3: Prepare Mono Cable
If you are using the pre-prepared mono cable from DigiKey, pictured in the component list, skip this step.

If using a different cable, you’ll need to prepare the wires for soldering:
- Cut the mono cable to length (typically 1 m).
- Strip off approximately 2 cm of the outer insulation.
- Then, separate the 2 individual inner wires. If there is one insulated wire plus copper strands, twist these copper strands together to be one of your wires.
- Strip off approximately 0.5 cm of insulation from the inner wires.
- For each inner wire, twist the inner strands
together
Step 4: Identify Mono Cable Wires
If using the pre-prepared DigiKey cable, you can skip this step.

You should use a multimeter or other continuity tester to confirm which wire corresponds to which part of the plug. Follow this guide for checking continuity (https://www.youtube.com/watch?v=T4p8UQZqh5U) to determine which wire corresponds to the Sleeve, and Tip of the mono cable plug.

Mono Plug | DigiKey mono cable | Your mono cable
Tip | Red
Sleeve | White

## MAKER GUIDE

Files available at https://github.com/makersmakingchange/Spruce-Mini-Joystick | Page 24 of 34
Step 5: Pre-tin Wires and Header Pins

Pre-tin the wires and the headers by melting a small amount of solder onto them so they are silver and shiny.

Do this to each of the 4 wires on the audio cable, both wires on the mono cable, and each of the 5 pins on the joystick unit.

## MAKER GUIDE

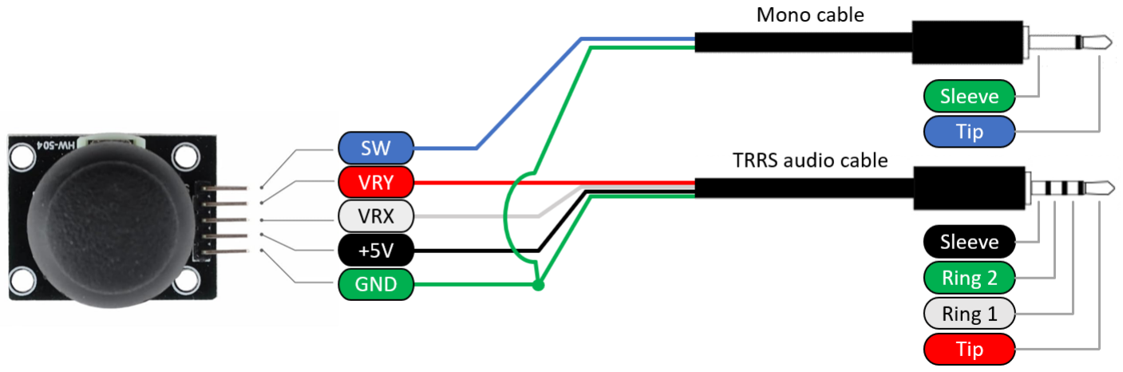
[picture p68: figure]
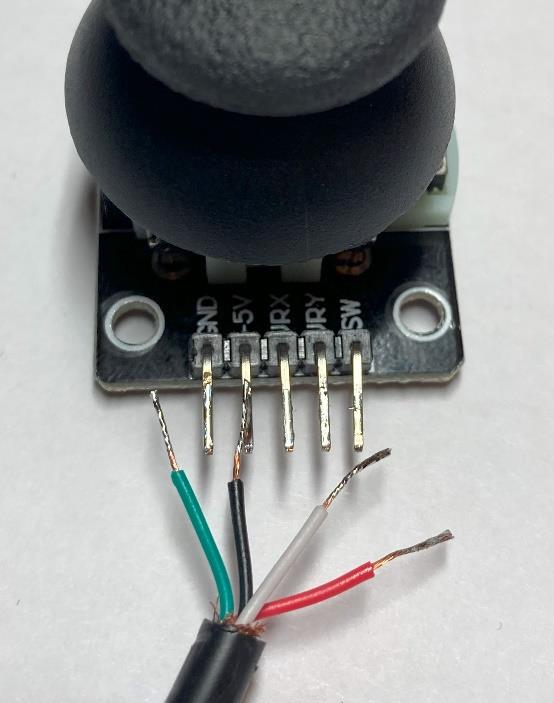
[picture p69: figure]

Files available at https://github.com/makersmakingchange/Spruce-Mini-Joystick | Page 25 of 34

Wiring diagram

JOYSTICK BOARD LABEL | DIGIKEY TRRS CABLE | TRRS PLUG | DIGIKEY MONO CABLE | MONO PLUG
SW | --- | --- | Red | Tip
VRY | Red | Tip | -- | ---
VRX | White | Ring 1 | -- | ---
+5V | Black | Sleeve | -- | ---
GND | Green | Ring 2 | White | Sleeve
Step 6: Solder Voltage (+5V) Pin

Take the wire from the TRRS audio cable that corresponds to the sleeve, line this wire up with the +5V pin on the joystick unit, and solder together.

On the audio cable from DigiKey, this will be the black wire.

Note: Try to get the insulation on the wire as close as possible to the edge of the header pin, so there is less wire that can move and touch other wires.

## MAKER GUIDE

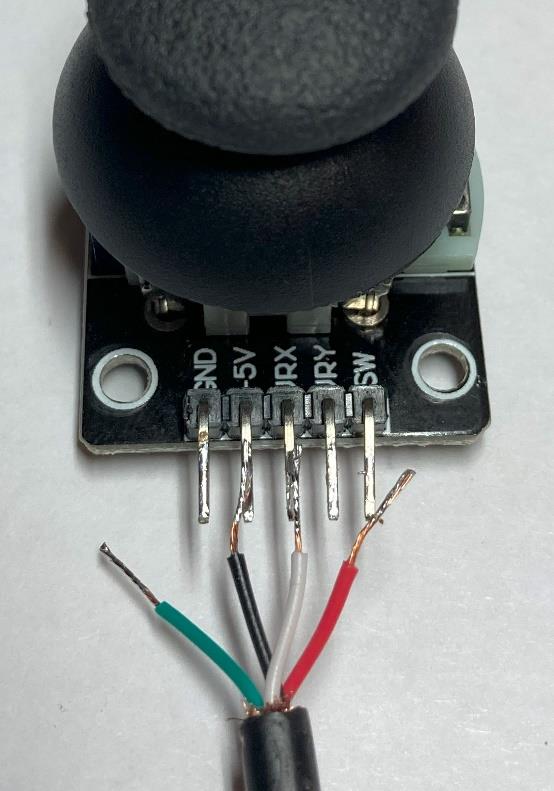
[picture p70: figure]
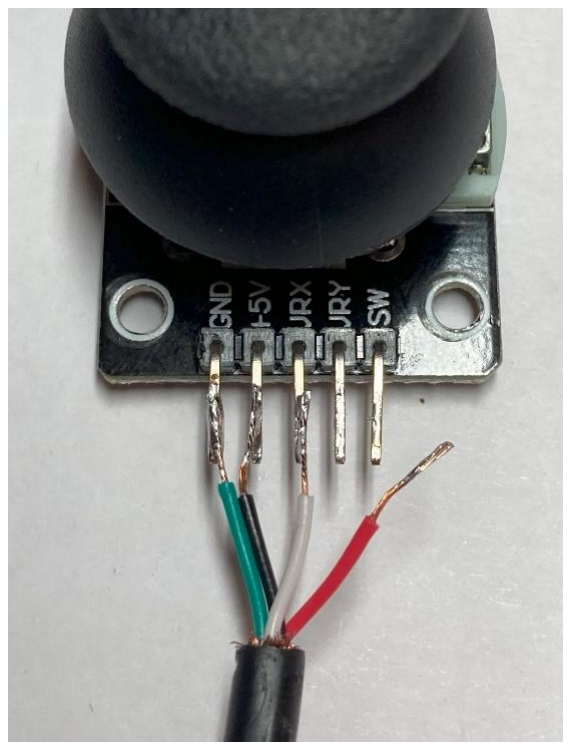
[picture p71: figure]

Files available at https://github.com/makersmakingchange/Spruce-Mini-Joystick | Page 26 of 34
Step 7: Solder X (VRX) Pin

Take the wire from the TRRS audio cable that corresponds to ring 1, line this wire up with the VRX pin on the joystick unit, and solder together.

On the audio cable from DigiKey, this will be the white wire.

Note: Try to get the insulation on the wire as close as possible to the edge of the header pin, so there is less wire that can move and touch other wires.

Step 8: Solder Ground (GND) Pin

Take the wire from the audio cable that corresponds to ring 2, line this wire up with the GND pin on the joystick unit, and solder together.

On the audio cable from DigiKey, this will be the green wire.

Note: Try to get the insulation on the wire as close as possible to the edge of the header pin, so there is less wire that can move and touch other wires.

## MAKER GUIDE

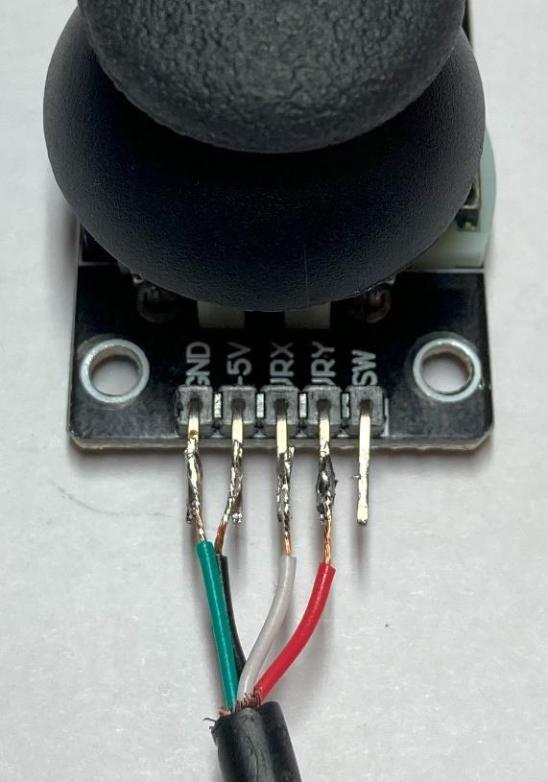
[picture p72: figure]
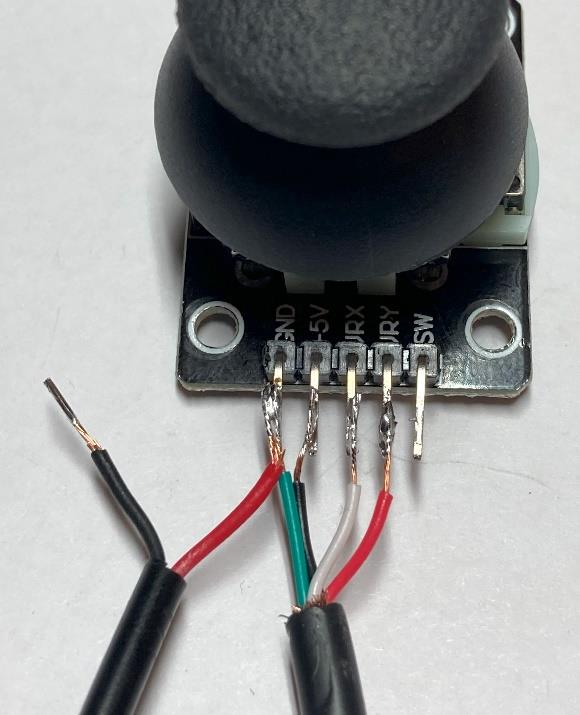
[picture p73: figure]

Files available at https://github.com/makersmakingchange/Spruce-Mini-Joystick | Page 27 of 34
Step 9: Solder Y (VRY) Pin

Take the wire from the audio cable that corresponds to the tip, line this wire up with the VRY pin on the joystick unit, and solder together.

On the audio cable from DigiKey, this will be the red wire.

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

Step 10: Solder Mono cable to Ground (GND) Pin

Take the mono cable wire which corresponds to the sleeve (white on the DigiKey cable) line it up with the GND pin on the joystick unit, and solder together.

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

## MAKER GUIDE

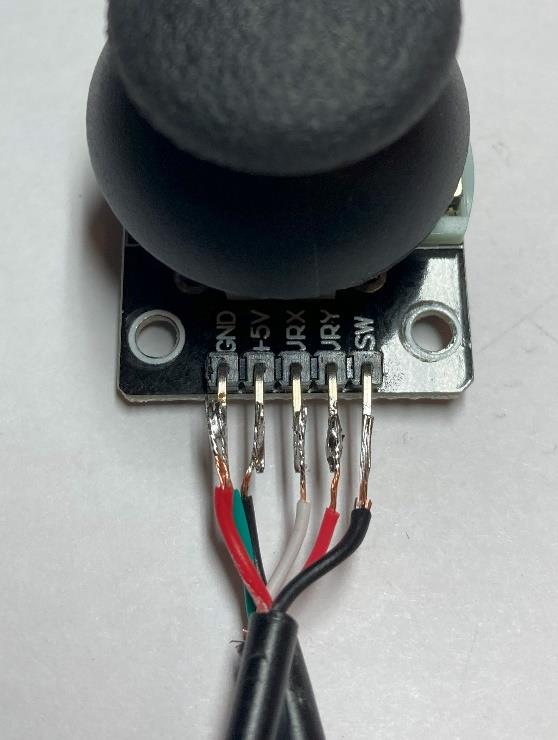
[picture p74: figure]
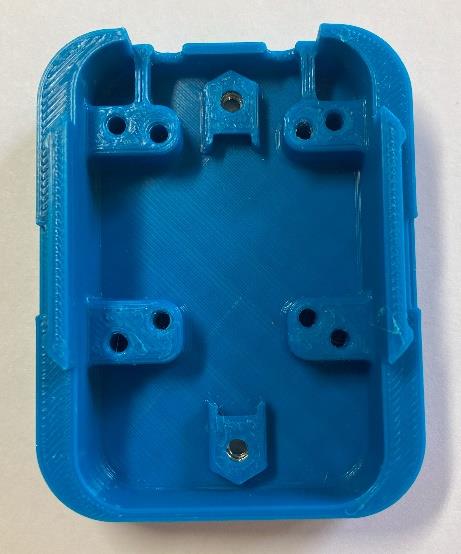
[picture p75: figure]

Files available at https://github.com/makersmakingchange/Spruce-Mini-Joystick | Page 28 of 34
Step 11: Solder Mono Cable to Switch (SW) Pin

Take the remaining wire from the
mono cable, line it up with the SW pin on the joystick unit, and solder together.

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

Step 12: Check for Shorts
Inspect the board and check that none of the connections are shorted.

There should be no
bridges/connections between adjacent pins.

If you have a multimeter, you can
use it to double check continuity.
Step 13: Insert M3 Hex Nuts into Enclosure Bottom

Take the enclosure bottom
and insert the M3 nuts into the slots as shown. You may require a tool such as
needle-nosed pliers or a
screwdriver to push the
nuts into place.

## MAKER GUIDE

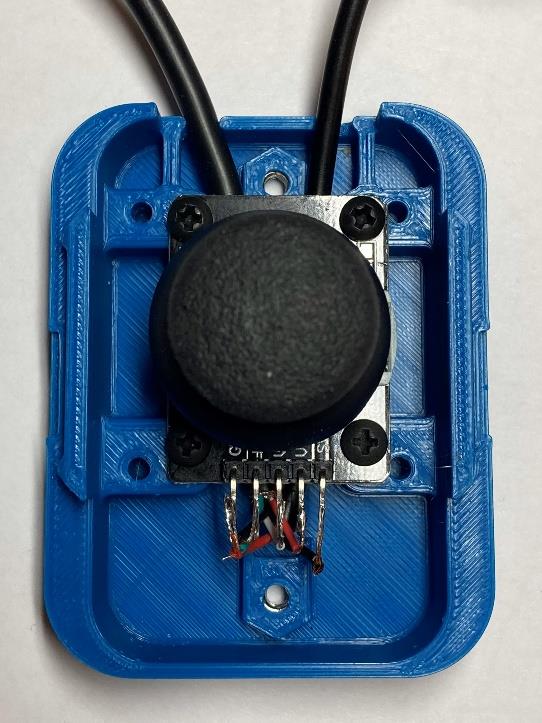
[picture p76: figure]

Files available at https://github.com/makersmakingchange/Spruce-Mini-Joystick | Page 29 of 34
Step 14: Position Joystick Unit

Thread the two cables from the joystick unit out the two cutouts at the back of the enclosure.

Ensure that the cables go between the screw holes and the captive nut piece and won’t interfere with screwing down the joystick.

Step 15: Screw in joystick unit

Position the joystick unit over the screw holes. There are two sets of screw holes for two different joystick units, find the set that matches your joystick module.

Screw in all four screws through the joystick unit and enclosure. Be careful not to over tighten.

## MAKER GUIDE


Files available at https://github.com/makersmakingchange/Spruce-Mini-Joystick | Page 30 of 34
Step 16: Check for Shorts
Visually inspect the board and check that none of the connections are shorted.

There should be no
bridges/connections between adjacent pins.

If you have a multimeter, you can use it to double check continuity.

Step 17: Fasten First Cable Tie
Thread the cable tie under the left cable and the 3D printed beam, going from the middle towards the edge.

Tighten the cable tie as much as you are able with your hands. The cable should now feel secure and unable to wiggle around.

Lastly, use flush cutters to cut off the excess cable tie.

## MAKER GUIDE


Files available at https://github.com/makersmakingchange/Spruce-Mini-Joystick | Page 31 of 34
Step 18: Fasten Second Cable Tie
Repeat with the second cable tie, thread the cable tie under the left cable and the 3D printed beam, going from the middle towards the edge.

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

Lastly, use flush cutters to cut off the excess cable tie.

Step 19: Assemble Enclosure

Line up the enclosure top and apply downward pressure to snap it into place.

Proceed to Testing.

## MAKER GUIDE

Files available at https://github.com/makersmakingchange/Spruce-Mini-Joystick | Page 32 of 34

Testing

Testing using a Multimeter
A multimeter can be used to test if the wires are connected and soldered correctly. It is most important to ensure that there is no short circuit between the Sleeve (Ground) and Tip (Voltage), as this can damage the host device. It can be tricky to place the probes and move the joystick, so tape, or a second person can be helpful here.

Note: The intended joystick for this build has two 10 KΩ potentiometers, but some joysticks use 5 KΩ potentiometers, which will result in the expected multimeter readings to be halved

Test 1: Testing for Short Circuits
1. Set the multimeter to measure resistance in the 1-
10 KΩ range.
2. Hold the tip of the red probe of the multimeter to the Sleeve (Voltage) of the TRRS cable.
3. Hold the tip of the black probe of the multimeter to Ring 2 (Ground) on the TRRS cable.
4. Confirm that the resistance is between 4 – 5 KΩ.
a. Between 4 – 5 KΩ: No shorts. Proceed to next test.
b. Less than 50 Ω: There is a short circuit between a Ground and Voltage pin (Pins 1, 3, 4, and 6). This must be fixed to prevent damaging a host device. Open the joystick and review/fix your soldering joints.
c. Other values: There is a wiring problem. Open the joystick and review/fix your soldering joints.

If you have no short circuits, you can move on to testing the joystick directions. This can be done with either the multimeter, or with a USB-HID gamepad that accepts an analog joystick.

Test 2: Testing Vertical Joystick Axis
1. Hold the tip of the red probe of the multimeter
to the Sleeve (Voltage) of the TRRS cable.
2. Hold the tip of the black probe to Ring 1 (Y-axis) on the TRRS cable.
3. While holding the multimeter probes in place, move the joystick fully in the UP ↑ direction.

## MAKER GUIDE

Files available at https://github.com/makersmakingchange/Spruce-Mini-Joystick | Page 33 of 34
a. You may require a second person to hold the probes in place or move the joystick.
b. Otherwise, the joystick can be held in place with some tape to leave your hands free to hold the multimeter probes in place.
4. Read the resistance on the multimeter:
a. Less than .05 KΩ: The Y-axis potentiometer is wired correctly.
b. Otherwise, review the wiring diagram and ensure your wiring matches.
5. Release the joystick back to neutral position.

Test 3: Testing Horizontal Joystick Axis
1. Hold the tip of the red probe of the multimeter to the Sleeve (Voltage) of the TRRS cable.
2. Hold the tip of the black probe to Tip (X-axis) of the TRRS cable.
3. While holding the multimeter probes in place, move the joystick fully in the RIGHT → direction.
a. You may require a second person to hold the probes in place or move the joystick.
b. Otherwise, the joystick can be held in place with some tape to leave your hands free to hold the multimeter probes in place.
4. Read the resistance on the multimeter.
a. Less than .05 KΩ: The X-axis potentiometer is wired correctly.
a. Otherwise, review the wiring diagram and ensure your wiring matches.
5. Release the joystick back to neutral position.

## MAKER GUIDE

Files available at https://github.com/makersmakingchange/Spruce-Mini-Joystick | Page 34 of 34

Test 4: Testing Push Button
1. Change the multimeter to continuity checking mode.
2. Hold the tip of the red probe to the Sleeve (Sel) of the mono cable.
3. Hold the tip of the black probe to the Tip (GND) of the mono cable.
4. While holding the probes in place, push on the joystick to activate the button.
a. You may require a second person to hold the probes in place or push the joystick.
b. Otherwise, the joystick can be held down with some tape to leave your hands free to hold the multimeter probes in place.
5. Listen for the multimeter to beep.
a. While the joystick is pressed, the multimeter should emit a sound.
b. When not pressed, the multimeter should be quiet.

Testing using an USB-HID Gamepad Device
1. Plug the joystick into analog joystick input for the host device.
a. X1 or X2 on an Xbox Adaptive Controller.
b. Plug the mono cable into the A switch jack on an Xbox Adaptive Controller.
2. Plug the host device into your laptop.
3. If using Windows, open “Set up USB Game Controllers” from the Control Panel. You can find this by searching your computer in the search bar next to the Windows icon.
a. If using a Mac, use https://hardwaretester.com/gamepad
4. Select the host device from the list of controllers and go to “Properties”.
5. Move your joystick and observe the movement of the cross hatch in the “Axes” window. Ensure it moves in the proper directions when you move the joystick (the arrow points in the up direction). If not, open the joystick and check your connections.
6. Push the joystick to activate the button.
a. You should see the button activate on whichever testing system you are using, respective of which switch port you plugged the cable into.

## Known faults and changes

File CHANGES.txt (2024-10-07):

October 7, 2024
 - User Guide updated to Version 1.0.1:
	- Added drift troubleshooting and instructions on the order to plug in the switch and joystick cables.
	- Updated compatibility by adding PlayStation Access Controller.

------------------------------------------------------------------------------------------------------
September 27, 2023
Version 1.0
 - Spruce Mini Joystick design and documentation, based off the Cedar Mini Joystick, uploaded to GitHub

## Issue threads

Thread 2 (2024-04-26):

### ISSUE TITLE
Push down button getting stuck inconsistently 

### ISSUE THREAD

**Issue by jversloot** [makersmakingchange/Spruce-Mini-Joystick#2]
On some builds, using the generic joystick module with headers, when the push button is tested on its own it works as expected, but when tested on the Forest Hub or XAC, when both the joystick and the switch are plugged in, at times the button appears to be pressed down after being released, as if it were "stuck on". If just the button is plugged in and not the joystick this doesn't happen, or if the joystick is plugged into the device (Forest or XAC) and the button is plugged into a switch tester this doesn't happen either.

**Comment by stephandobri** [comment]
Bug fixed. Cause was connecting the tip of the mono cable to the ground pin on the generic PS2 joystick module.
The Maker Guide was updated to have makers double check the wires corresponding to the tip and sleeve of the mono cable, and telling them which needs to be connected to ground.

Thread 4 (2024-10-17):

### ISSUE TITLE
Generic Joystick Component Drift

### ISSUE THREAD

**Issue by tjfentie** [makersmakingchange/Spruce-Mini-Joystick#4]
In the BOM there are two versions of the joystick module to buy, the adafruit and the generic one. The generic one [Link](https://www.amazon.ca/dp/B07VXPFB9Q?ref=cm_sw_r_cso_cp_apin_dp_JCV5F8YBPY93H0SNAY4T_2&ref_=cm_sw_r_cso_cp_apin_dp_JCV5F8YBPY93H0SNAY4T_2&social_share=cm_sw_r_cso_cp_apin_dp_JCV5F8YBPY93H0SNAY4T_2&starsLeft=1&skipTwisterOG=1) seems to have some inconsistency when it comes to quality of orders resulting in drift in the final built device.

We need to determine if we pull the generic one from the BOM/instructions and just suggest Adafruit module to avoid broken units.

**Comment by jversloot** [comment]
Drift is only present when used with the Xbox Adaptive Controller (XAC) and is due to the built-in autocalibration. This issue has been resolved by providing instructions on the order to plug in the joystick cable and switch cable when using with the XAC. Instructions are in the User Guide, and on the website posting, and a brief warning is on the README.

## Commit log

2023-09-29 v1.0 updates
    [Spruce Mini Joystick v13.step, Spruce_Joystick_BOM.csv, Spruce_Joystick_BOM.xlsx, Spruce_Mini_Joystick.f3z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]
2023-12-14 Updated Adafruit wiring diagram
2023-12-14 Add files via upload
    Updated Adafruit wiring diagram
2024-01-18 Updated Maker Guide to correct wiring
2024-02-12 Fixed error in wiring diagram for generic PS2 joystick
2024-04-15 Updated Maker Guide
    Added clarification in assembly steps for the Adafruit joystick to describe the orientation of the joystick, and the side to thread the wires into.
2024-07-05 Update README.md
    Step 4 read "Assemble the Oak Compact Joystick" and I changed it to "Spruce Mini Joystick".
2024-10-17 Added mount adapter files
    [Joystick RAM Mount Adapter v5.f3d, Joystick_Camera_Mount Narrow v3.f3d, Joystick_Camera_Mount_Adapter.stl, Joystick_RAM_B_Mount_Adapter.stl]
2026-04-01 Added Topper Files
    Added topper 3D files. Same as the ones included in the Cedar. Attribution added for AbleGamers toppers where the files originated.
    [Ball_Topper.stl, Concave_Topper.stl, Convex_Topper.stl, Large_Goalpost_Topper.stl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]
2026-04-01 Update README.md
    Added mounting info
